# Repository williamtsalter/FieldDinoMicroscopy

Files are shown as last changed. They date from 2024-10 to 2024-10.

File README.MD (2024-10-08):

# FieldDino

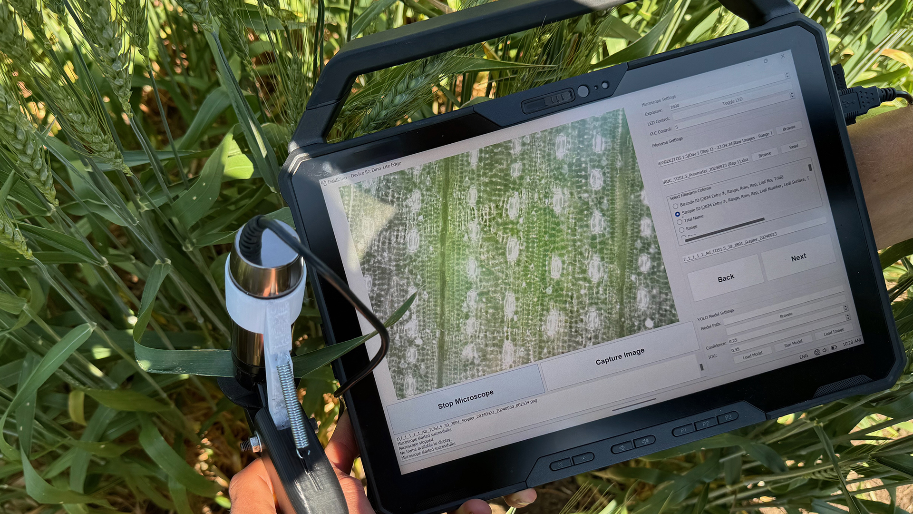
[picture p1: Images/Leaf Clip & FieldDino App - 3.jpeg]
FieldDino


FieldDino is a Python-based application that enables simple control of Dino-LITE microscopes in the field, for fast phenotyping of large scale field trials. Filenames are loaded in from an Excel spreadsheet based upon the sampling order. The app is also capable of running live YOLO segmentation in the field for measurement of stomatal traits using pre-trained models. FieldDino is designed for field researchers who need to capture, analyse, and annotate microscopic images in real-time.

We also include the 3D print files and instructions for a leaf-clip style microscope mount. We have designed the leaf clip to ease focussing in the field, speeding up image capture and standardising image brightness and scale across large data collection campaigns.

***Note that the FieldDino leaf clip and software were designed to work with the Dino-Lite AM7515 series of USB microscopes, however, should also work with other microscopes in the Dino-Lite range with modifications.***

<details>
  <summary><h1 style="font-size:10vw">3D printed leaf clip microscope mount</h1></summary> 

The leaf clip should be 3D printed in two parts, the handle and the microscope mount/trigger. Note that we have provided different mount files depending on the magnification of your microscope. The mount should be printed in white (to diffuse the microscope LEDs) whilst the colour of the handle does not matter so much. We recommend using PETG filament, using supports whilst printing and using glue on the print bed to improve bed adhesion. We also recommend printing using fine (0.12 mm layers). After 3D printing, remove all support material and clean up print if needed using sandpaper.

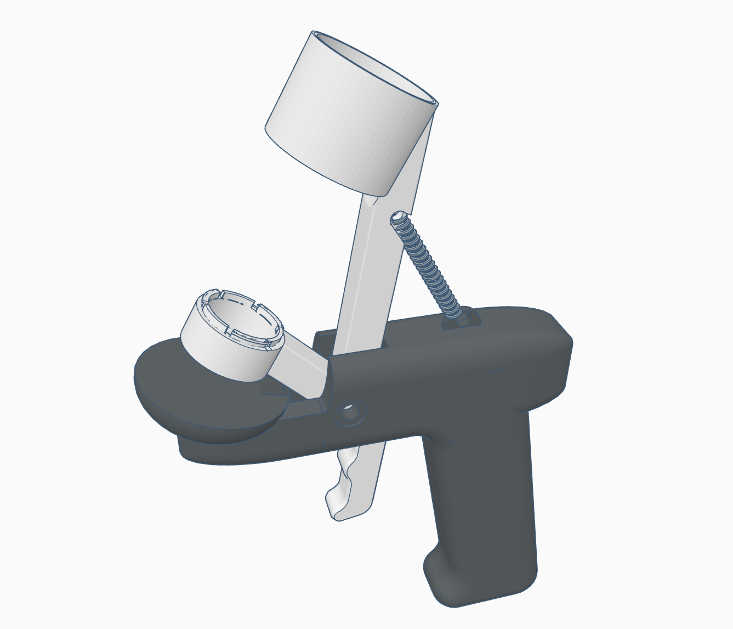
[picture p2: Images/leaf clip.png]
Leaf clip
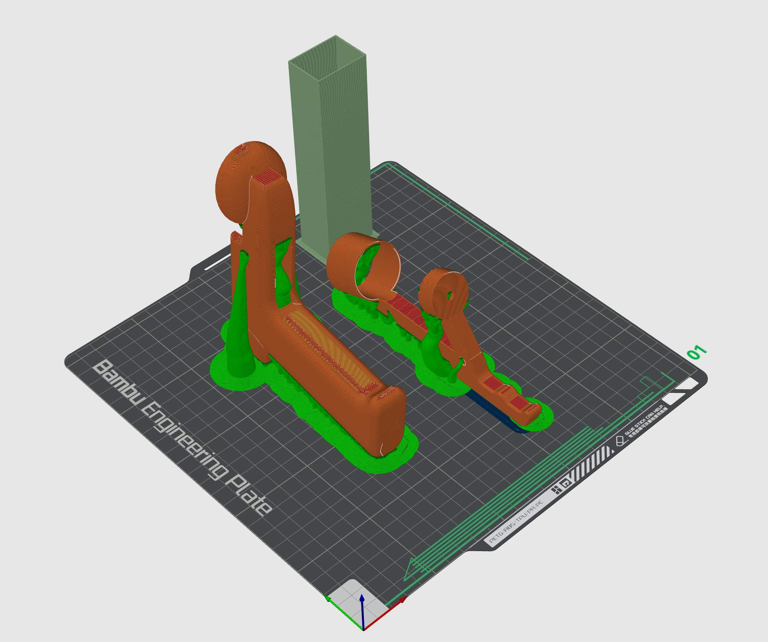
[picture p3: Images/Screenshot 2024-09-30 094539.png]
3D print bed
|||
|------------- | ------------- |

To assemble the leaf clip you will need some additional items that you can get from a hardware store:
- 3 mm thick EVA foam
- 38.1 mm x 6 mm extension spring
- 1 x 40 mm M5 bolt, 1 x nut and washers
- Threadlock to stop nut from coming loose during use
- Black electrical tape

Once you have all the parts above, you can assemble the leaf clip as follows: 

|Step | Image |
|------------- | ------------- |
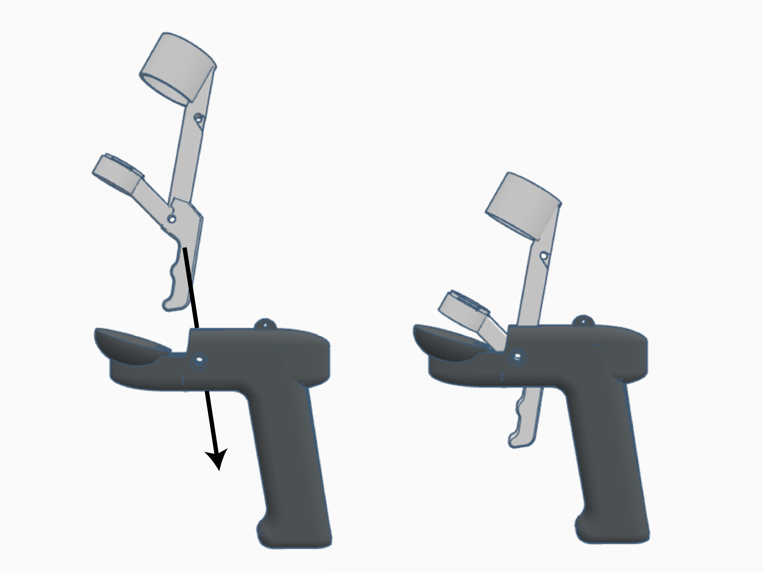
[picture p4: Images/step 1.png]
step 1
|1. Slot the mount into the handle, lining up the bolt hole. You can use washers if there is a biut of a wiggle to the trigger ||
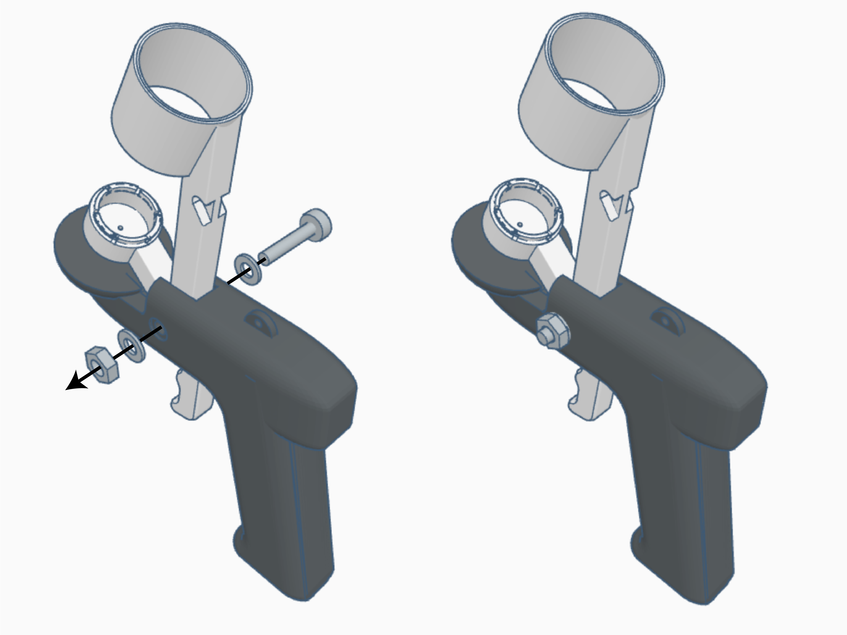
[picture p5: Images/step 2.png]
step 2
|2. Using the bolt, nut and washers, secure the handle in place. Use threadlock to secure nut in place without overtightening | |
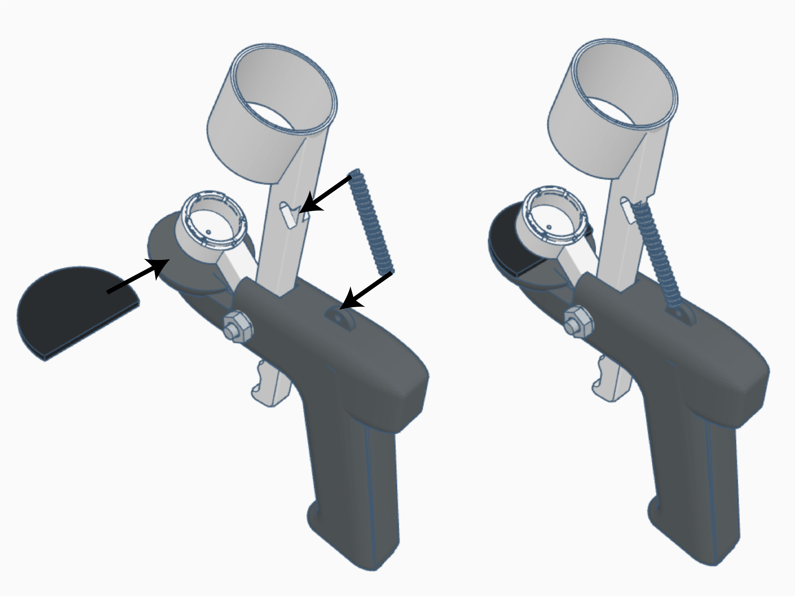
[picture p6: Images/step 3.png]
step 3
|3. Stick gasket foam to the handle and secure spring in place ||
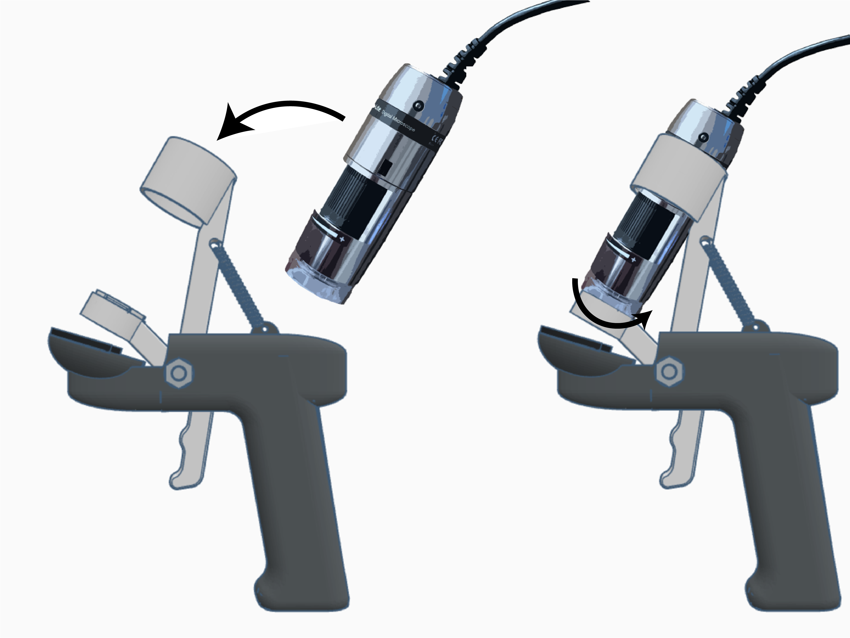
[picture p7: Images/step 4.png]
step 4
|4. Insert microscope into mount and twist to lock in place | |
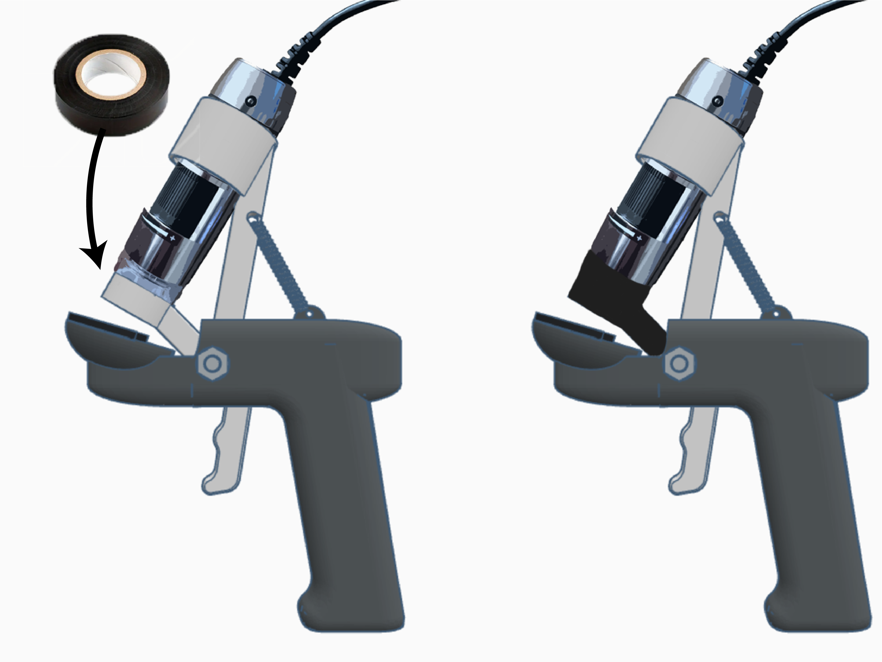
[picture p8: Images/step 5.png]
step 5
|5. Tape around transparent plastic and sides of mount cap with three layers of black electrical tape | |

</details/>
  
<details>
  <summary><h1 style="font-size:10vw">FieldDino Python app <em>(Windows only for now)</em></h1></summary> 

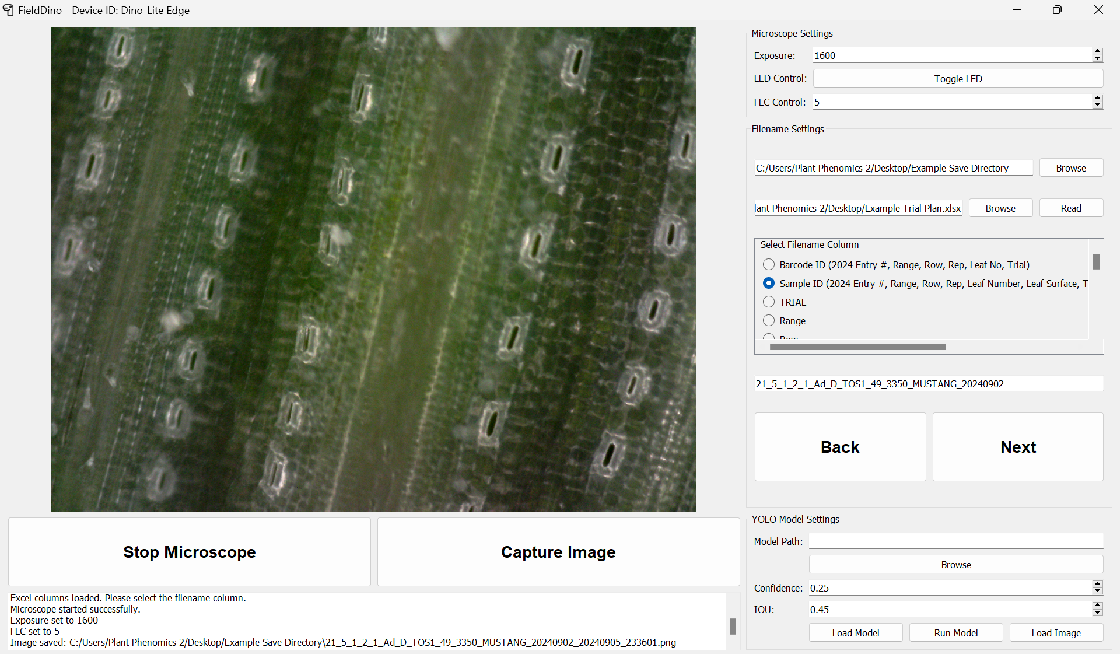
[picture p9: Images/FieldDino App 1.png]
FieldDino App


## Features

- **Microscope Control**: Interface with Dino-Lite digital microscopes for live image capture.
- **Image Processing**: Capture, save, and analyze both live and static images.
- **YOLO Integration**: Load and run YOLO models for object detection on microscope feeds or static images.
- **Customizable Settings**: Adjust microscope parameters like exposure and LED state.
- **Flexible File Naming**: Customize image filenames with field-specific information.

<details>
  <summary><h2 style="font-size:7vw">FieldDino app prerequisites</h2></summary> 

<details>
  <summary><h3 style="font-size:5vw">Python installation</h3></summary> 

1. Install Python version 3.7-3.10 (https://www.python.org/)

2. Find the location of the Python executable file that you just installed, it will likely be in the following location:
        ```
        C:\Users\<USER>\AppData\Local\Programs\Python<version>
        ```
3. Open Windows Settings -> System -> About -> Advanced System Settings -> Environment Variables
    
4. Inside the upper window labeled 'User Variables' select 'Path' and edit
    
5. Select 'New' and add file directory for the location above
    
6. Select 'New' and repeat previous step for the Scripts folder within the Python<version> directory
  
7. Restart computer

</details>

<details>
  <summary><h3 style="font-size:5vw">Virtualenv install and test</h3></summary> 
1. Open a new command prompt (Windows Key + R, cmd.exe)

2. Install virtualenv through the command ```pip install virtualenv```

3. Check that virtualenv is installed through the command ```pip list```

4. Install virtualenvwrapper-win through the command ```pip install virtualenvwrapper-win```

5. Create a test environment with the command ```mkvirtualenv testenv```. Note this will also make a folder called Envs in your user directory

6. To leave an environment use ```deactivate```

7. You can re-enter an environment by using ```workon <environmentname>``` and from there can invoke package installations like ```pip install```

8. To completely delete an environment make sure you leave the environment first and use ```rmvirtualenv <environmentname>``` to delete the environment

</details>
  
<details>
  <summary><h3 style="font-size:5vw">Install Git for Windows</h3></summary> 
1. In a browser window navigate to the [Git download page](https://git-scm.com/downloads/win), download the standalone installer
    
2. Open the installer executable and follow the on screen prompts
  
3. Restart computer

</details>

<details>
  <summary><h3 style="font-size:5vw">Install .net Framework 3.5</h3></summary> 
1. In a browser window navigate to the [Microsoft Download Centre](https://www.microsoft.com/en-au/download/details.aspx?id=21) to download the installation file

2. Run the installer executable and follow on screen prompts

</details>

<details>
  <summary><h3 style="font-size:5vw">Request and install DinoLite SDK</h3></summary> 
1. In a browser window navigate to the [Dino-Lite software page](https://www.dino-lite.com/download06.php) and request the SDK license agreement
    
2. Once you receive a link to download the SDK, download and unzip the folder, then run the installer executable and follow on screen prompts
    
3. Ensure the Dino-Lite SDK is installed in the correct location, noting that `DNX64.dll` should be in `C:\Program Files\DNX64\DNX64.dll`.

</details>
</details>  

<details>
  <summary><h2 style="font-size:7vw">FieldDino app installation</h2></summary> 

We are now ready to install required packages for FieldDino using a requirements file. For reference, the required packages include:
- PyQt5
- OpenCV
- Openpyxl
- PyTorch CPU
- Ultralytics YOLO

1. Open a new command prompt and clone the GitHub repository:
   ```
   git clone https://github.com/williamtsalter/FieldDino.git
   cd FieldDino
   ```
2. Create a virtual environment for FieldDino using the command ```mkvirtualenv FieldDino```. To open this when you want to use the app, use the command ```workon FieldDino```

3. Install required Python packages from requirements file:
   ```
   pip install -r requirements.txt
   ```
4. If you want to run a model in real time, place your YOLO model file (`.pt`) in the project directory or any accessible location.

5. If you want to quickly run the app after install you can run the FieldDino.bat file. This batch file will open the FieldDino virtual environment then open the app. Note, you can also create a shortcut to this file to run from the Desktop.
        
</details>

<details>
  <summary><h2 style="font-size:7vw">FieldDino app usage</h2></summary> 

1. Open a new command prompt, open the FieldDino virtual environment (```workon FieldDino```), navigate to the FieldDino folder (```cd FieldDino```) then start the application:
   ```
   python app.py
   ```
   <em>OR</em>

   Open the FieldDino folder in File Explorer, run the FieldDino.bat file. Note that you can also create a shortcut to this file on your desktop for quick and easy access.

2. **Microscope Control**:
    - Ensure microscope is connected to the computer.
    - Click "Start Microscope" to initialize the Dino-Lite microscope.
    - Adjust exposure and LED settings in the "Microscope Settings" panel.
    - Note that we have removed the ability to control axial illumination as it gave very harsh reflections.

3. **Custom filename loading from Excel or CSV file**
    - Select browse to identify an Excel file containing filenames in a column
    - Click read to load in column names, select the column containing filenames
    - Note, if you capture an image you need to replace (e.g., out of focus, captured by accident) you can press back to return to the previous filename in the column
  
4. **Image Capture**:
    - Set the save directory and customize filename prefixes in the settings.
    - Click "Capture Image" to save the current view and move to the next filename, if an Excel file has been uploaded.

5. **YOLO Model Integration**:
    - Load a YOLO model using the "Load Model" button.
    - Set confidence and IOU thresholds.
    - Click "Run Model" to start object detection on the live feed.

| Original                                                                                                                        | Processed                                                                                                                      |
|---------------------------------------------------------------------------------------------------------------------------------|--------------------------------------------------------------------------------------------------------------------------------|
| 1_B_I_R1_20230907 | Processed Image |

6. **Static Image Analysis**:
    - Click "Load Image" to analyze a pre-captured image.
    - Run the YOLO model on the loaded image for object detection.

7. **Settings**:
    - Customize file naming conventions in the "File Naming" section.
    - Set the save directory for captured images.
    - Adjust model parameters in the "YOLO Model Settings" section.

8. **Advanced settings**
    - For even more control, you can edit the app.py file before starting the software.

</details>

<details>
  <summary><h2 style="font-size:7vw">FieldDino app troubleshooting</h2></summary> 
- Ensure the Dino-Lite microscope is properly connected to the computer before starting the application. Note we have tested the app thoroughly with USB cable connections only, not the WI-FI DinoLite models.
- If you still struggle to connect the microscope, you can open the app.py file and edit lines 63 and 64 changing the ```self.device_index``` and ```self.cv2_cam_index``` variable. These tend to depend on the number of cameras embedded or connected to the computer. You can run ```python cameralist.py``` to identify connected cameras and microscopes.
- If the YOLO model fails to load, check the file path and ensure it's a compatible `.pt` file.
- For issues with image capture, verify that the save directory exists and is writable.
        
</details>
</details>

<details>
  <summary><h1 style="font-size:10vw">Contributing to FieldDino</h1></summary>

Contributions to FieldDino are welcome! Please fork the repository and submit a pull request with your improvements.

</details> 

<details>
  <summary><h1 style="font-size:10vw">License</h1></summary>

[MIT Open Source License](https://opensource.org/license/mit)

</details>

<details>
  <summary><h1 style="font-size:10vw">References and credits</h1></summary>        

Icon Source:
<a href="https://www.flaticon.com/free-icons/jurassic" title="jurassic icons">Jurassic icons created by Marz Gallery -
Flaticon</a>
        
</details>

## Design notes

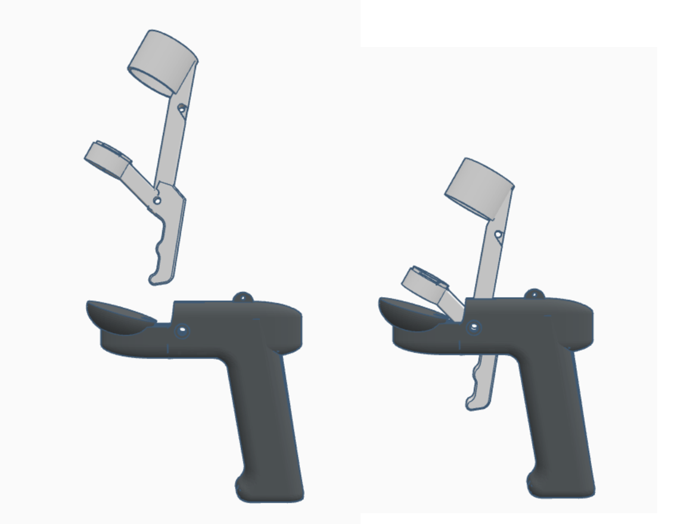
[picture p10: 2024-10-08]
Images/Screenshot 2024-09-30 142124.png

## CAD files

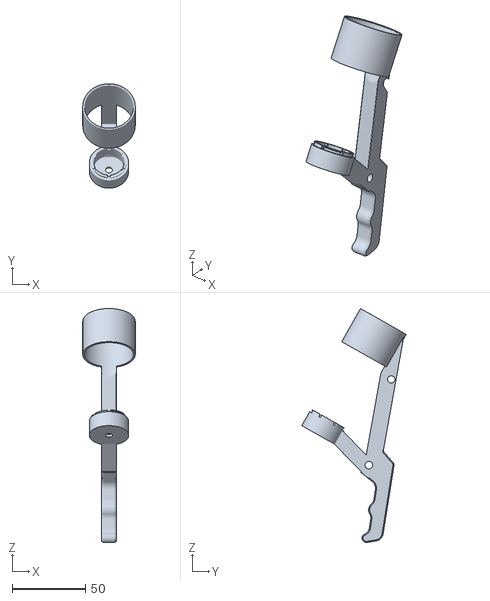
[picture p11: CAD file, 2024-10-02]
3D print files/Edge series mount.stl
36.0 x 71.5 x 160.2

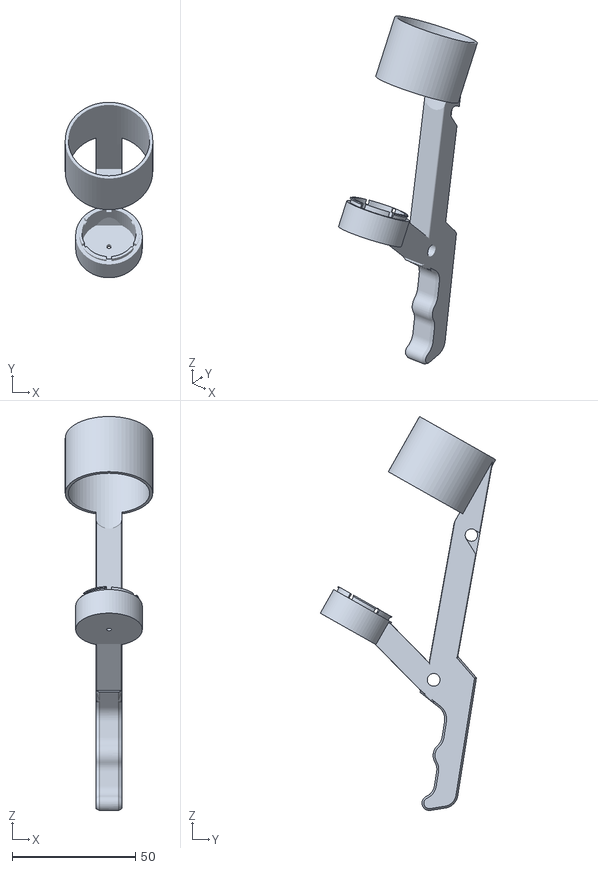
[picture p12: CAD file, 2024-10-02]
3D print files/900x mount.stl
35.5 x 71.1 x 159.7

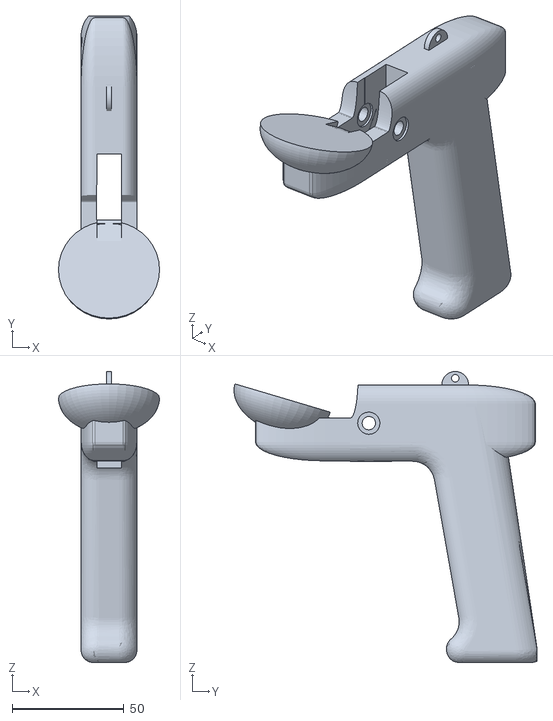
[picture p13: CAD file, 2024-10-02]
3D print files/Leaf clip base.stl
45.3 x 135.6 x 130.3

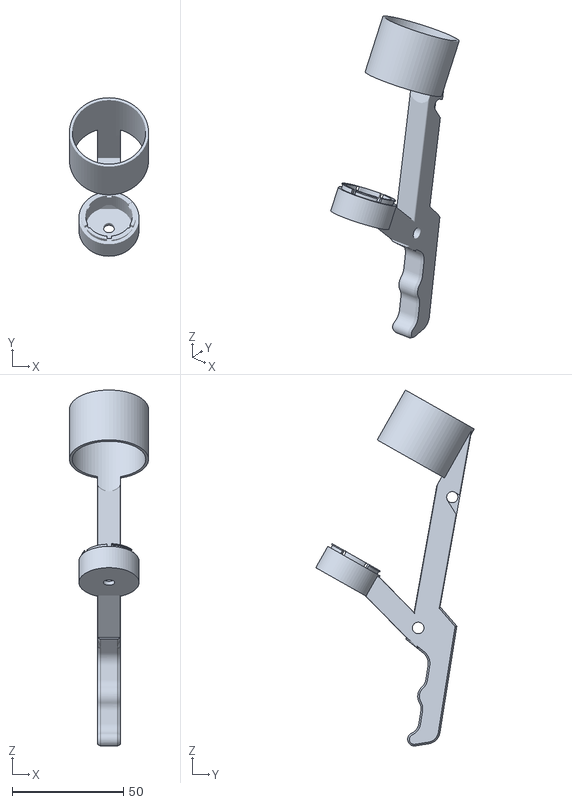
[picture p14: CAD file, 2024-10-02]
3D print files/200x to 400x mount.stl
35.5 x 71.1 x 159.7
